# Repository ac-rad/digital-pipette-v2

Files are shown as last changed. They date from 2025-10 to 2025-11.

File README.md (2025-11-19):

# Digital Pipette v2


This directory contains CAD files and programs for the Digital Pipette v2 introduced in [Commit: Digital pipette: open hardware for liquid transfer in self-driving laboratories](https://doi.org/10.1039/D5DD00336A).
It is the successor to the original Digital Pipette introduced [here](https://doi.org/10.1039/D3DD00115F) and avaliable on GitHub [here](https://github.com/ac-rad/digital-pipette).

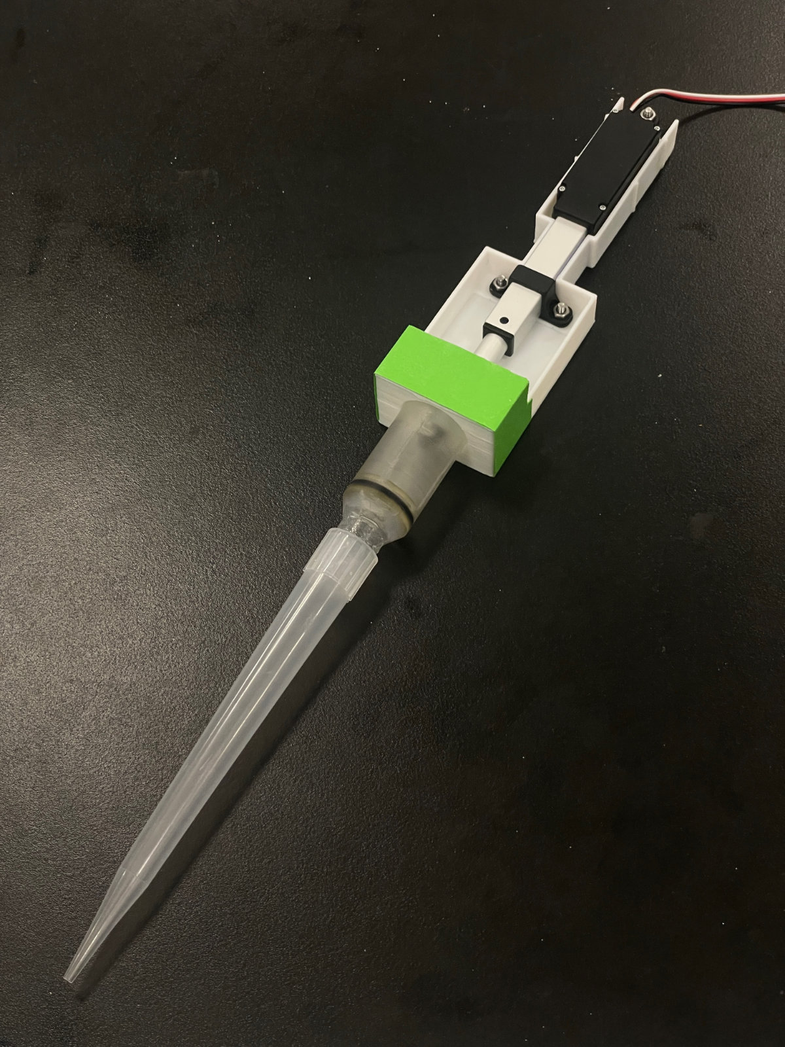
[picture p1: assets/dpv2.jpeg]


## Bill of Materials
| Item | Quantity | Description |
| --- | --- | --- |
| [Linear actuator](https://www.actuonix.com/l16-50-63-6-r) | 1 | Actuonix L16-50-63-6-R |
| [DC 6V power supply](https://www.actuonix.com/dcpowersupply) | 1 | DC Linear Actuator Power Supply* |
| [Arduino](https://store-usa.arduino.cc/products/arduino-uno-rev3) | 1 | Arduino Uno Rev3** |
| [Pipette Tips](https://www.sigmaaldrich.com/CA/en/product/sigma/z740090?srsltid=AfmBOoqENiqRej9o1Fh8WpmBl-x27AytvgyorUww807KblMdqG__zZBk) | - | Sigma-Aldrich BRAND pipette tips, 1-10 mL |
| [O-ring](https://www.amazon.ca/dp/B0DKJ5TKH8) | 1 | Approx. inner diameter of 17 mm, width of 2.5 mm
| [Grease](https://www.dupont.com/products/molykote-high-vacuum-grease.html) | - | MOLYKOTE High-Vacuum Grease, DuPont
| Short screws & nuts | 3 | M3 10 mm screws and M3 nuts were used |
| Long screw & nut | 1 | M3 20 mm screw and M3 nut were used |

>Basic electronic parts (e.g. breadboard, cables, soldering iron, etc.) are not included in this list.

>\* Any other DC 6V power supply should work.

>** Any other Arduino-compatible boards should work.

## Electric Circuit
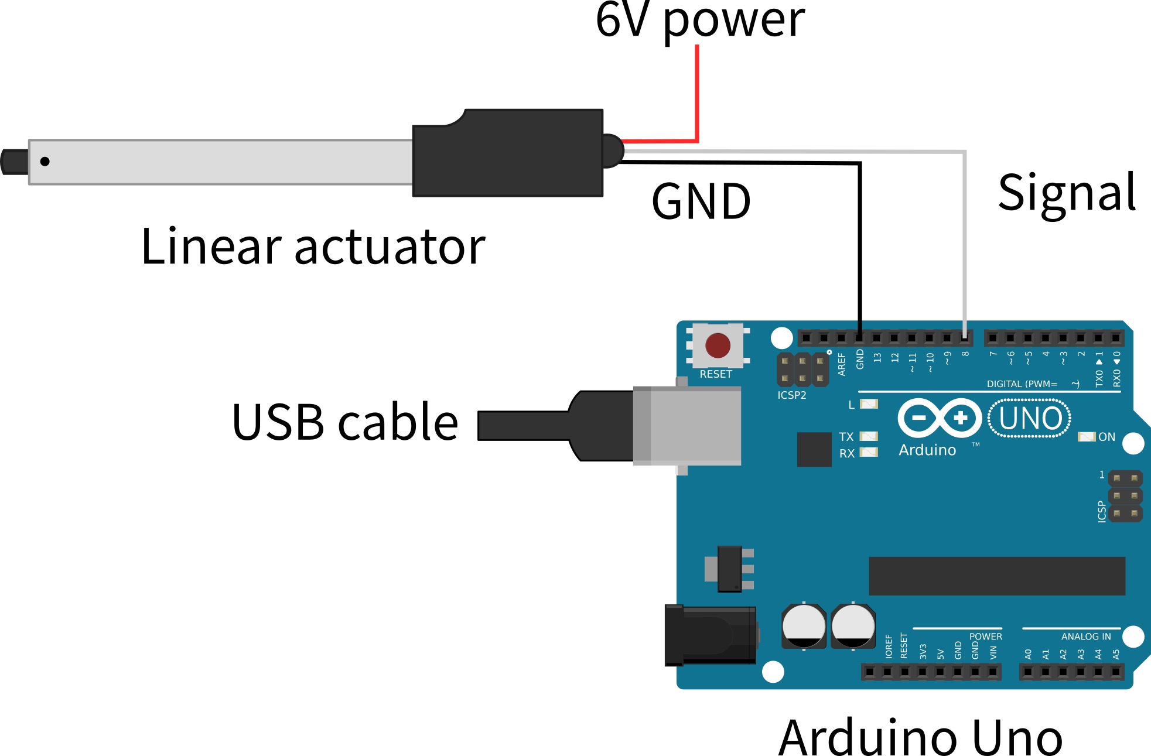
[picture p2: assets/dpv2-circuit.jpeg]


Although it is not drawn explicitly, **ensure that the GND of Arduino and DC 6V power supply are connected**.

**Caution**: When connecting the power supply, ensure that the voltage and polarity match the specifications of the control board. Incorrect wiring may damage the circuit or cause injury. Build and use the device at your own risk.

### Example Setup
You can connect the Arduino, the linear actuator, and the 6V power supply using jumper wires and alligator cables. This setup works for development, but it is not recommended for production since cables get easily become disconnected. Soldering wires is recommended to make connections more stable. The example shown below uses a perfboard to solder cables and connectors.

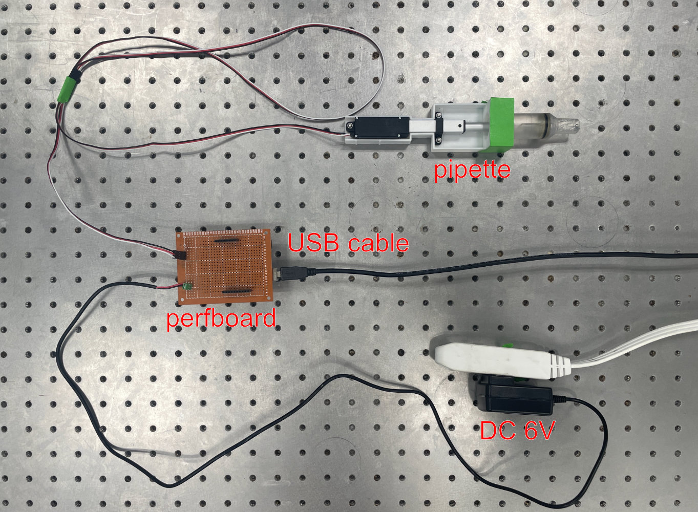
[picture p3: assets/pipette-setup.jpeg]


## Build Instructions

We will refer to the 3D printed components by the following names:  (a) Pipette, (b) platform, (c) syringe, (d) plunger, and (e) cover.

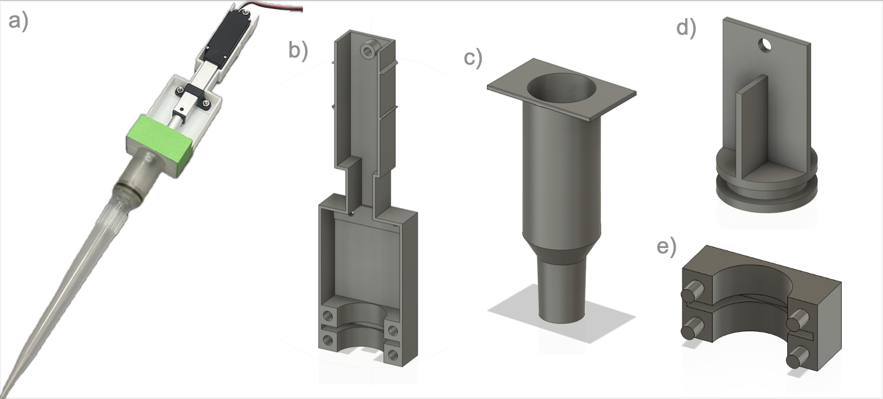
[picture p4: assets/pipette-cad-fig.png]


### Step 1
Prepare items shown in the bill of materials. Print the [platform](https://github.com/ac-rad/roboculture/blob/main/digital-pipette-v2/stl/dpv2_platform.stl), [plunger](https://github.com/ac-rad/roboculture/blob/main/digital-pipette-v2/stl/dpv2_plunger.stl), [syringe](https://github.com/ac-rad/roboculture/blob/main/digital-pipette-v2/stl/dpv2_syringe.stl) and [syringe cover](https://github.com/ac-rad/roboculture/blob/main/digital-pipette-v2/stl/dpv2_cover.stl) with a 3D printer. We printed the platform and the cover using white [ANYCUBIC PLA](https://store.anycubic.com/products/pla-filament?variant=28613838635068) with a [KP3S printer](https://kingroon.com/products/official-kingroon-kp3s-3d-printer?srsltid=AfmBOoouSShLhwt5UxNMyRfsJzguQAaet1WOk76gDIyBJmFdmgcyfKbj), and the syringe and plunger pieces were printed with [Clear Resin V4](https://formlabs.com/store/materials/clear-resin-v4/?srsltid=AfmBOorUXbHxEBsoq4NVLikjujRHokVETI2yYDyIPURNv1b0i4osuqV6) using a [Form 3L printer](https://formlabs.com/3d-printers/form-3l/?srsltid=AfmBOopiq-vRPgbCmxs518tfKLkiUMFvQhNmBW-FyH8gnUD7D1ZHYR3r). 

### Step 2
Connect the end of the linear actuator to the plunger piece with a short screw and a nut.

### Step 3
Place an O-ring in the groove of the plunger piece. NOTE: Applying a thin strip of electrical tape (~3 mm wide) in the groove before placing the O-ring can help achieve a tighter seal.

### Step 4
Apply grease to the end of the plunger piece over the O-ring, and inside the syringe piece. Place the plunger piece inside the syringe.

### Step 5
Place the linear actuator into the platform such that the top of the syringe piece lies in the groove of the platform. Secure the actuator in place with the plastic parts shipped with the actuator. We placed a flat mounting strap underneath the actuator and the U-shaped bracket piece on top of the actuator, and used two short screws (10mm) and nuts to secure everything to the platform. We used a long screw (20mm) and nut to secure the top of the actuator to the top of the platform.

### Step 6
Place the cover piece over the syringe to hold it to the platform. OPTIONAL: Use tape to secure the cover.

### Step 7
Connect the linear actuator with the electric circuit.

## Source code
The [src](https://github.com/ac-rad/roboculture/blob/main/digital-pipette-v2/src) directory contains example code to operate the Digital Pipette v2.
- `pipette.ino` is an example Arduino sketch
- `controller.py` is an example Python program to send serial commands from PC to the Arduino

You may need to install [pySerial](https://pyserial.readthedocs.io/en/latest/) to run the Python example.

## Citation
If you find this useful in your research, please consider citing as below.

```
@article{yoshikawa2025commit,
      title={Commit: Digital pipette: open hardware for liquid transfer in self-driving laboratories}, 
      author={Naruki Yoshikawa and Kevin Angers and Kourosh Darvish and Sargol Okhovatian and Dawn Bannerman and Ilya Yakavets and Milica Radisic and Alán Aspuru-Guzik},
      year={2025},
      doi={10.1039/D5DD00336A},
}
```

## License
The pipette is licensed under the [Creative Commons Attribution 4.0 International License][cc-by].

[][cc-by]

[cc-by]: http://creativecommons.org/licenses/by/4.0/
[cc-by-image]: https://i.creativecommons.org/l/by/4.0/88x31.png

The source code is licensed under the MIT license.

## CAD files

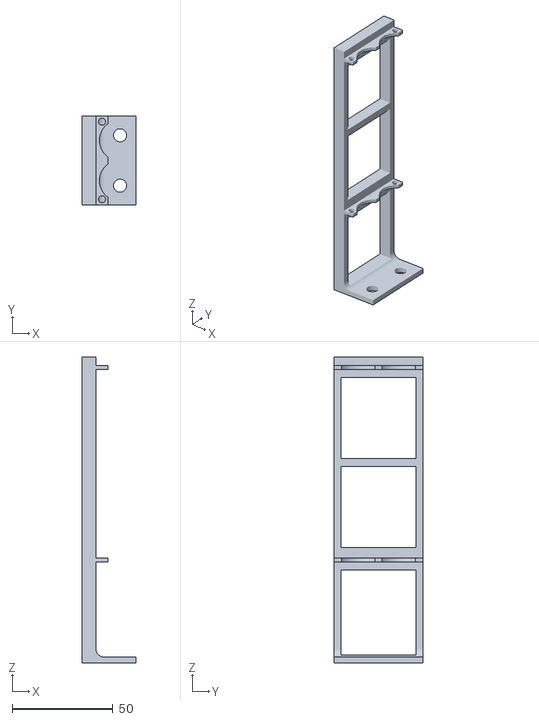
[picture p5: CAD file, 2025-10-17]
stl/tiprack_left_stand.stl
27.0 x 44.0 x 152.0

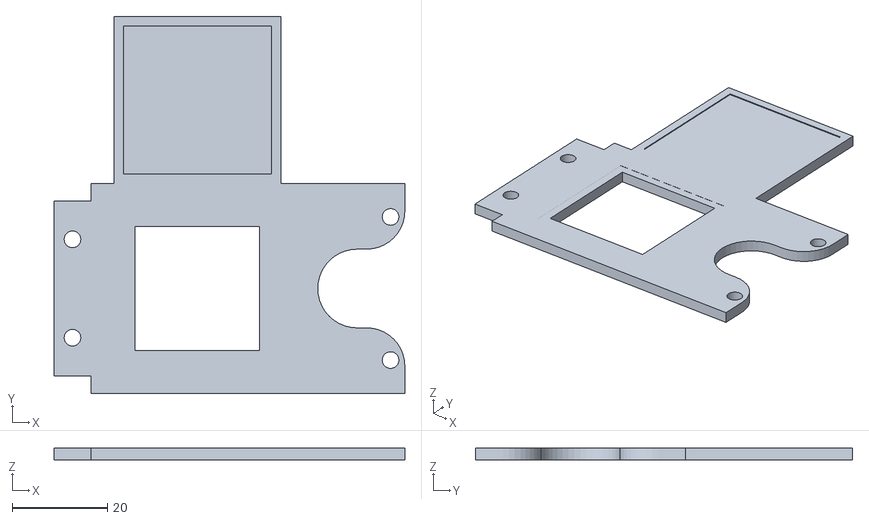
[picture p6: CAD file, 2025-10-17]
stl/tipremover_tag_holder_right.stl
73.5 x 79.0 x 2.50

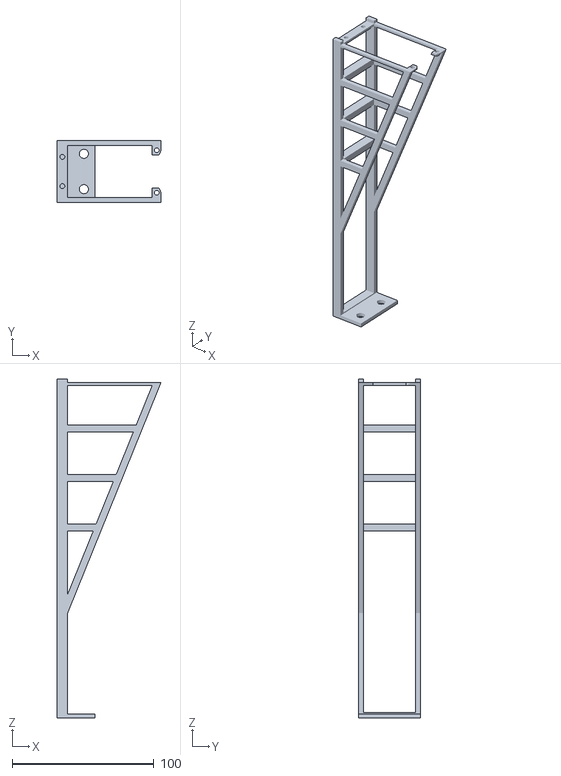
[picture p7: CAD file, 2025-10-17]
stl/tipremover_stand.stl
73.5 x 44.0 x 239.4

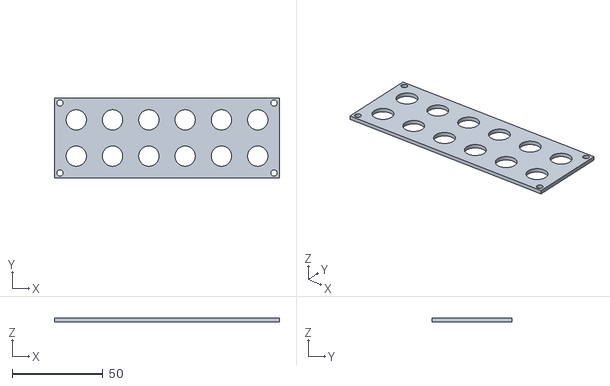
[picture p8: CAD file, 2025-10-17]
stl/tiprack_bottom.stl
124.0 x 44.0 x 2.00

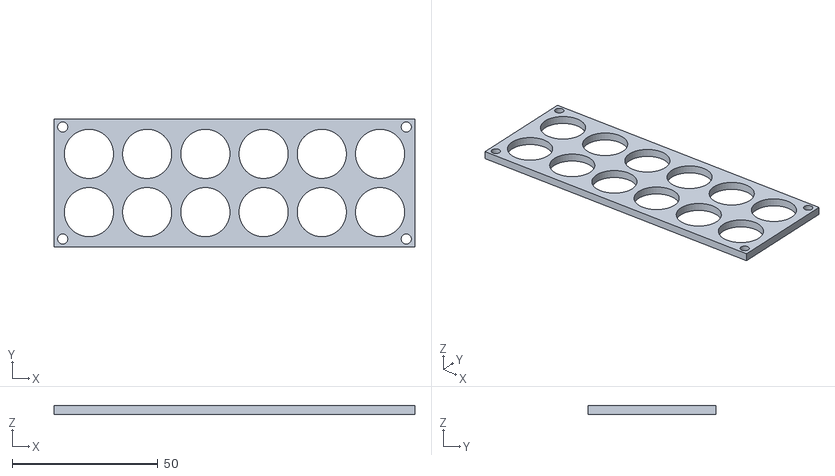
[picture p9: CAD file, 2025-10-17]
stl/tiprack_top.stl
124.0 x 44.0 x 3.00

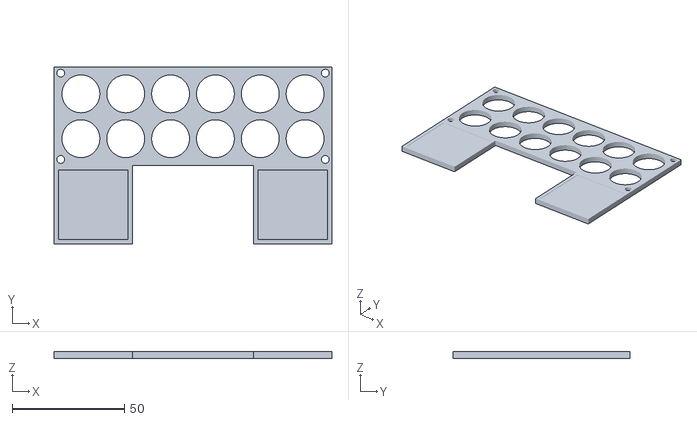
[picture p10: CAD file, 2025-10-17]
stl/tiprack_top_tag_holders.stl
124.0 x 79.0 x 3.00

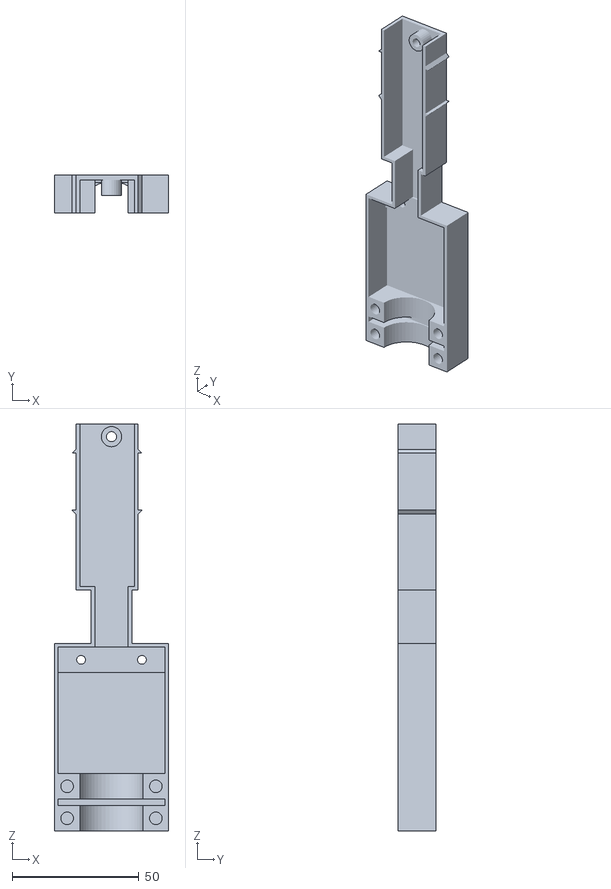
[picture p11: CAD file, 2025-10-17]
stl/dpv2_platform.stl
45.0 x 15.0 x 160.5

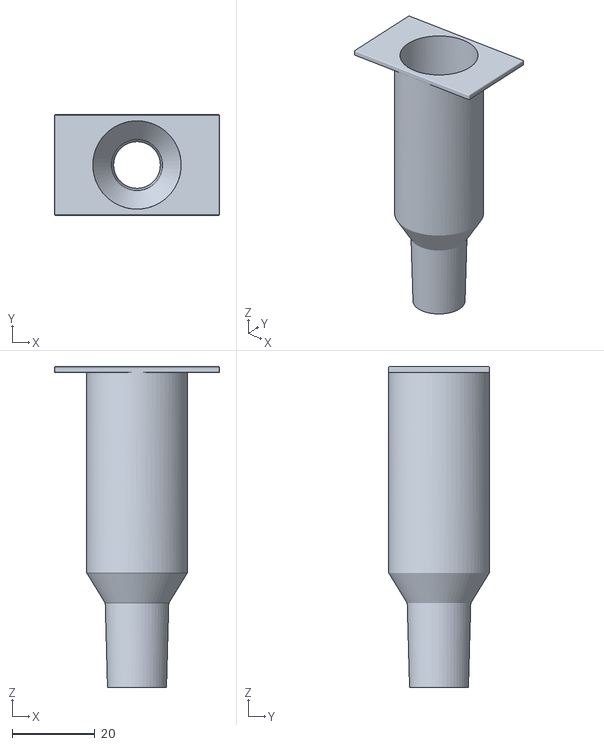
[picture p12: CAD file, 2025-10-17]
stl/dpv2_syringe.stl
40.0 x 24.4 x 77.8

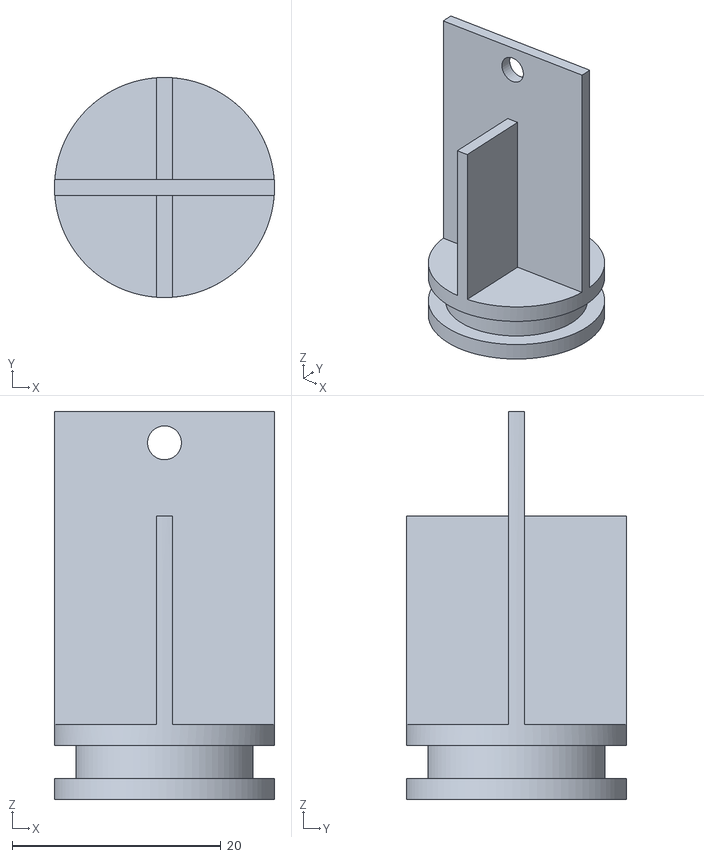
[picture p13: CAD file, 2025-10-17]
stl/dpv2_plunger.stl
21.1 x 21.1 x 37.2

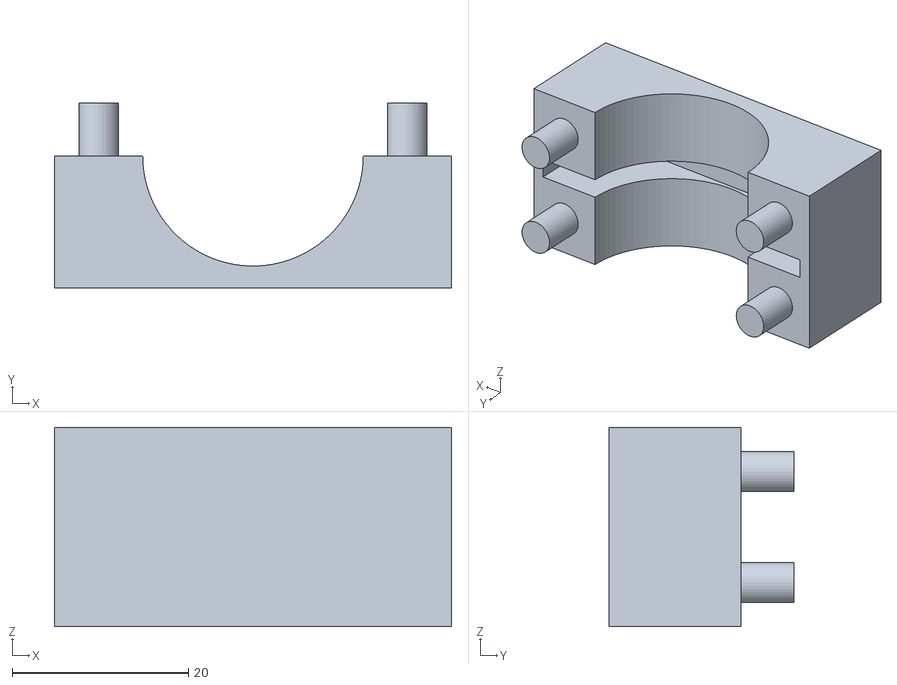
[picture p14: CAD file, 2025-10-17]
stl/dpv2_cover.stl
45.0 x 21.0 x 22.6

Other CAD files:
stl/tiprack_right_stand.stl
stl/tipremover_tag_holder_left.stl
f3d/dpv2_cover.f3d
f3d/dpv2_platform.f3d
f3d/dpv2_plunger.f3d
f3d/dpv2_syringe.f3d
f3d/pipette_tip_rack.f3z
f3d/pipette_tip_remover.f3z

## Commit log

2025-10-17 Add pipette tip rack and pipette tip remover stl files
    [tiprack_bottom.stl, tiprack_left_stand.stl, tiprack_right_stand.stl, tiprack_top.stl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]
2025-10-17 Add tip rack and tip remover f3z
    [pipette_tip_rack.f3z, pipette_tip_remover.f3z]
